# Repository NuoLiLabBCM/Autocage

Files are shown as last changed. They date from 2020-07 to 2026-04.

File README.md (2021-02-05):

# Autocage
A home-cage system for fully autonomous mouse behavioral and optogenetic experiments
## Features
- Automated home-cage training in challenging decision-making tasks with voluntary head-fixation
- Unsupervised optogenetic experiment to survey brain regions involved in behavior
- Running standalone, with GUI monitoring multiple parallel systems
- Protocols for automated training in voluntary head-fixation, delayed response task, and contingency reversals

## System Overview
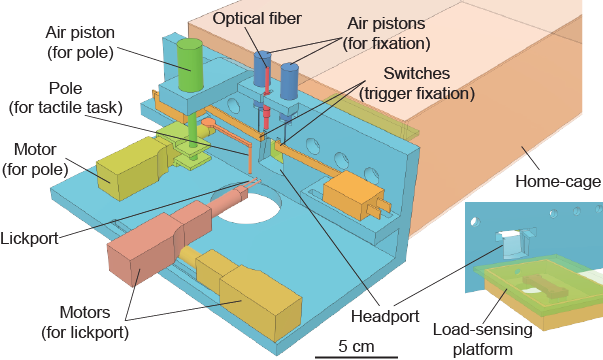
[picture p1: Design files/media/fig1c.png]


## Citation
Hao, Thomas, and Li. (2020) Fully autonomous mouse behavioral and optogenetic experiments in home-cage. https://doi.org/10.1101/2020.12.27.424480 

## Contact
Further information and requests should be directed to and will be fulfilled by the Lead Contact, Nuo Li (nuol@bcm.edu)

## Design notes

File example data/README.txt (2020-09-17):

/* There are six files in the folder for each mouse, They are:
 * PARAS.TXT:	parameters for task/trials
 * PARAF.TXT:	parameters for head-fixation
 * TRIALS.TXT:	data for each trial
 * EVENTS.TXT:	data for each event
 * EVENTST.TXT:	data for the detailed events for each trial
 * WEIGHT.TXT:	weight data read from scale (20 Hz sample rate, 
 * 				only record weights > 10 g); ONLY available in version 1.0
 */

/*************TRIALS.TXT*************
 * 
 * Each row is for one trial;
 * 
 * Column1: Unix time when the trial is finished;
 * Column2: trial number;
 * Column3: ProtocolType: 10-Fixation; 21-Sample; 22-Delay; 23-Optostim
 * Column4: subProtocol number: 0-fixation; 1~9-sample; 10~18-delay; 19-optostim
 *			0: from begining to head-fixation for 25 sec; Sample = 1.3 sec, random 
 *			   	delay (0.2~0.5 sec), no error trials
 *			1: autoLearn ON, random delay (0.3~0.6 sec), no error trials, 
 *				advance: reach 100 trials;
 *			3: autoLearn ON, random delay (0.3~0.6 sec), with error trials, advance: 
				reach 200 trials;
 *			4: autoLearn antiBias, random delay (0.3~0.6 sec), advance: performance > 75%
 *			13: antiBias, Delay = 0.3 sec, forced delay, advance: performance > 70%
 *			14: antiBias, Delay = 0.5 sec, forced delay, advance: performance > 70%
 *			15: antiBias, Delay = 0.8 sec, forced delay, advance: performance > 70%
 *			16: antiBias, Delay = 1.0 sec, forced delay, advance: performance > 70%
 *			17: antiBias, Delay = 1.3 sec, forced delay, advance: performance > 70%
 *			18: antiBias, Delay = 1.3 sec, forced delay, timeOut->4 sec, 
 *				advance: performance > 70%, fixation duration 30->60 sec
 *			19: antiBias, Delay = 1.3 sec, 15% trials with stimulation during sample/delay/response
 * Column5: Trial type: 0-right; 1-left; 2-either side
 * Column6: Trial outcome: 0-No Response; 1-Reward; 2-Time Out (error); 3-'Others'
 * Column7: Optostim flag: percentage of power (10, 30, 50, 70 100%) + stim epoch (1-stim during sample; 2-delay; 3-response)
 *			e.g., 11 means stim during sample with 10% power
 *			0 means no stimulation in this trial.
 * Column8: Forward/Backward motor position: 0-255
 * Column9: Left/Right motor position: 0-255 (70 is roughly the center)
 * Column10-end: States visited in this trial (see state machine coded in Arduino_Master.ino)
 * 
 **************TRIALS.TXT*************/

/*************EVENTS.TXT*************
 * 
 * Each row is one event recorded.
 * 
 * Column1: Time stamp for the event; if the event is 1, the time is Unix time; 
 * 			otherwise it is milisec after restart.
 * Column2: Event type: 1-Arduino restarted; 7-switchTriggered; 8-headfixation; 
 *			11-headfixation again immediately after release
			9-release1:timeup; 10-release2:escape; 12-release3:struggle
			20~22-user updating FB_motor_position, LR_motor_position and FB_final_position;
 * Column3: Event value: -1 means N/A, otherwise is value corresponding to the event.
 * 
 **************EVENTS.TXT*************/

/*************EVENTST.TXT*************
 * 
 * Each row is for one trial
 * 
 * Column1: Trial number;
 * Column2: Number of events in this trial;
 * Column3~end: pairs of event ID and timestamp
 * 				ID: 39-timeup (see state machine coded in Arduino_Master.ino for details); 
 *					0-left lickport in; 1-left lickport out; 
 *					2-right lickport in; 3-right lickport out;
 * 				timestamp: unit: 0.1 ms; 0 is start of a trial
 *
 **************EVENTST.TXT*************/

/*************WEIGHT.TXT*************
 *
 * Each row is a 2-sec data segment
 * 
 * Column1: Unix time when the data were sent;
 * Column2-41: weight data sampled at 20 Hz
 *
*************WEIGHT.TXT*************/

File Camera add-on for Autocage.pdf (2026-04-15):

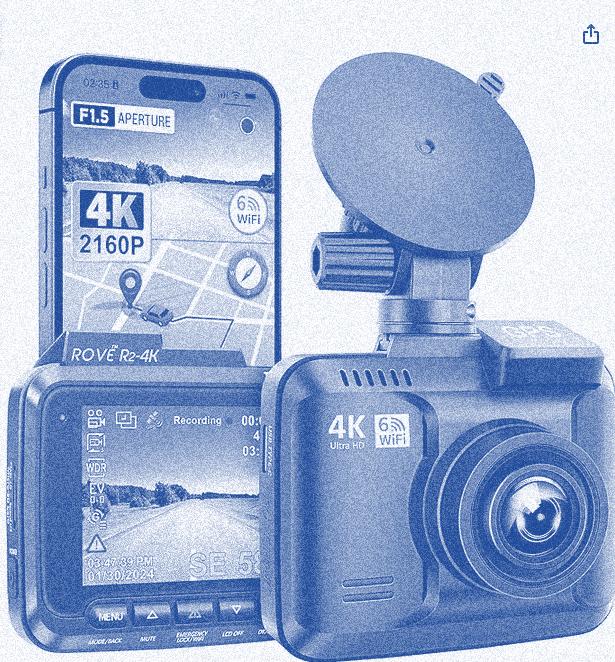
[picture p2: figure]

# add-on Camera to Autocage

# Part List:

Vender | Part # | Description | Unit Price
Amazon | R2-4K PRO | ROVE R2-4K PRO Dash Cam, Supports 512GB Max | $129.99
Amazon | MB-MD512SA/AM | SAMSUNG PRO Plus microSD Memory Card + Adapter, 512GB | $49.99
Amazon | UTC1211USP-WH | Amazon Basics 12W One Port USB-A Wall Charger (2.4A) Pack of 2 | $5.1
ThorLabs | FGB25 | Ø25 mm BG3 Colored Glass Bandpass Filter, 315 - 445 nm and 715 - 1095 nm | $40.70
ThorLabs | LA1134 | N-BK7 Plano-Convex Lens, Ø1", f = 60 mm, Uncoated | $24.43
ThorLabs | SM1L03 | SM1 Lens Tube, 0.30" Thread Depth, One Retaining Ring Included | $13.15
DigiKey | 365-1056-ND | EMITTER IR 890NM 150MA T 1 3/4 | $1.13
DigiKey | CF14JT39R0CT-ND | RES 39 OHM 5% 1/4W AXIAL | $0.04
| | Total | $264.93

# Hardware Setup

### - Camera Setup:

- Get a ROVE R2-4K PRO dash cam.
- Mount a lens (f=60mm) with a filter to the camera. The filter is for filtering out the masking LED light (RED).
- Insert a SAMSUNG 512G microSD memory card.
- Power on the dash cam.
- Follow the user manual to setup the camera settings via Setting Menu. You can do the settings either on the camera screen directly, or on your smartphone by connecting to the dash cam Wi-Fi and using ROVE APP.
- Key settings:
- Video Resolution: 1080P 1920x1080 @30FPS. (with 512G SD Card, you can get about 5 days’ data).
- Loop Recording: 1-Min,3-Min, 5Min or 10 Min.

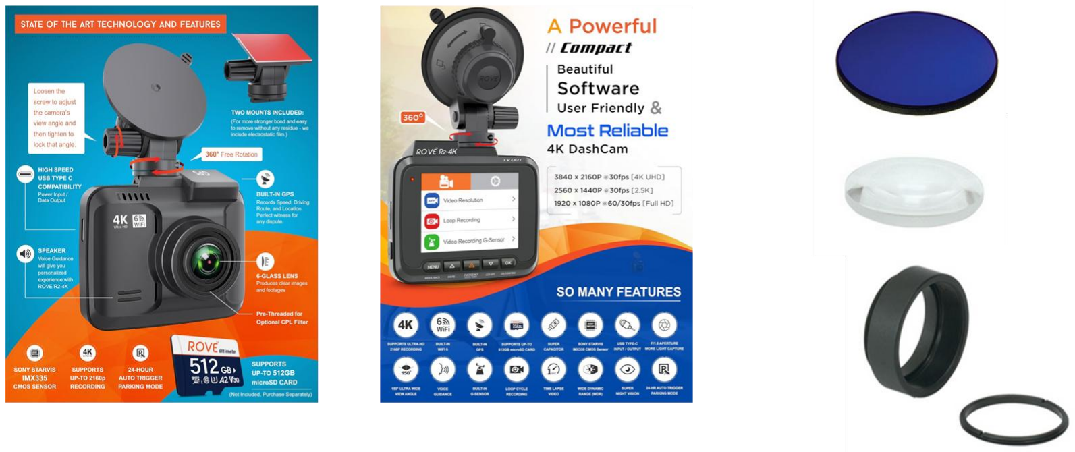
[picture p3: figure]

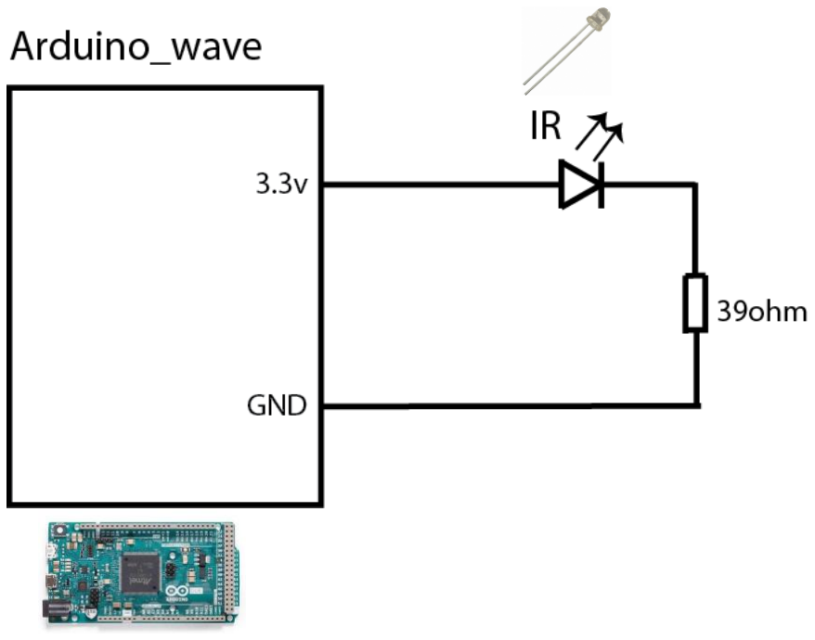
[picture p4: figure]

- IR Illuminator
- Get an Infrared Emitter and a 39 Ohm resistor.
- Assemble and connect the IR Illuminator to the existing Arduino DUE board (wave) as shown in the diagram.

# Add-on Camera layout inside Autocage

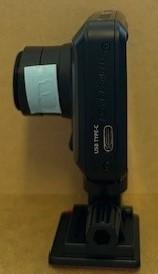
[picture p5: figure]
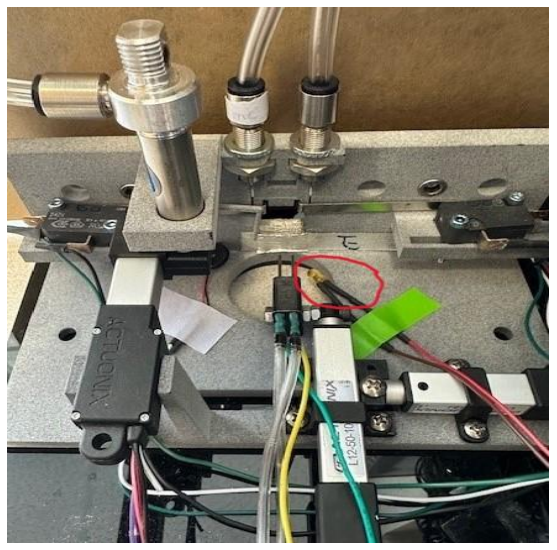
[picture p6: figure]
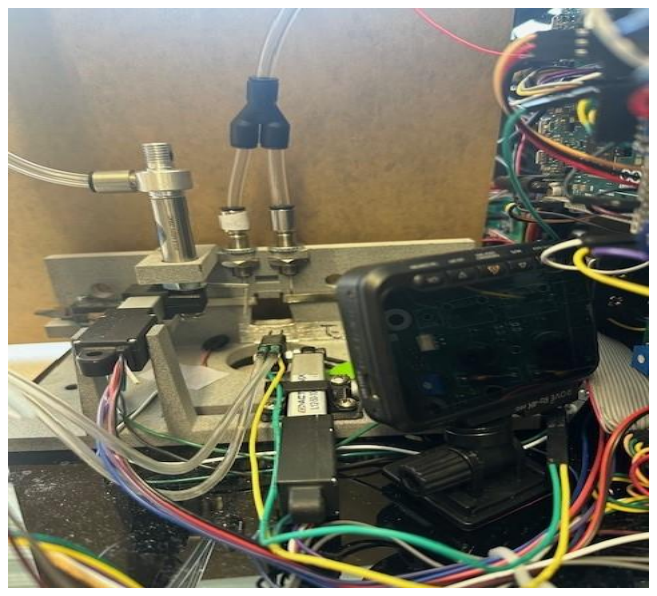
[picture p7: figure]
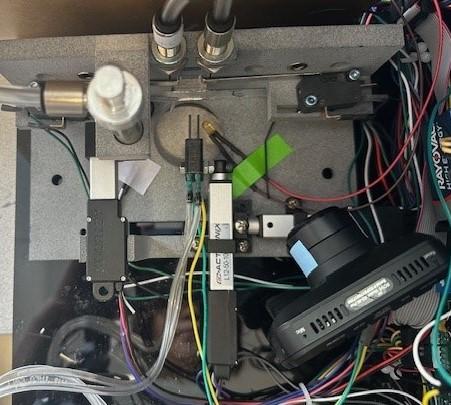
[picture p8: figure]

IR Illuminator | Front view | Top view | Side view

# Video Example

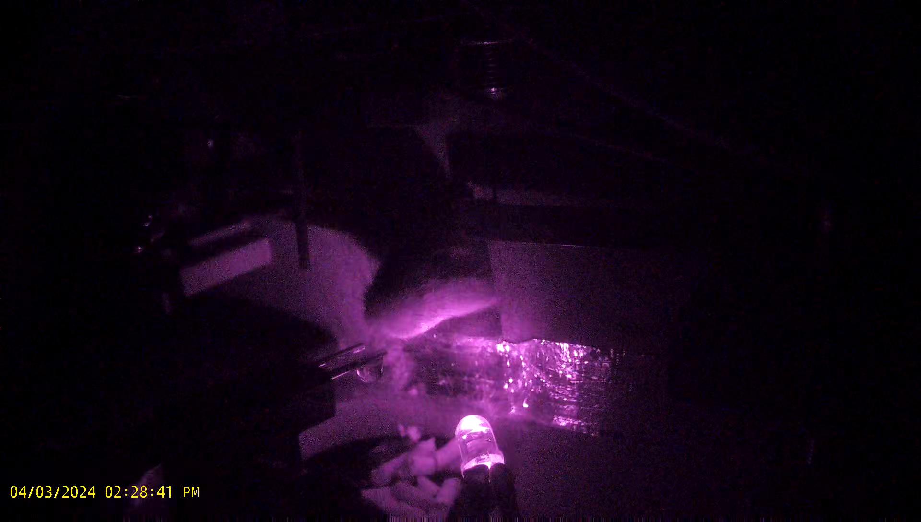
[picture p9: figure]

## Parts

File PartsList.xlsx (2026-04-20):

Part | Vendor | Item no. | Item description | Qty per Cage | Unit Price | Each Cage | Note
Enclosure | McMaster-carr | 8505K745 | Scratch-Resistant Acrylic BLACK 1/8 | 1.167 | $45.58 | $53.18
 | McMaster-carr | 8505K758 | Scratch-Resistant Acrylic BLACK 1/4 | 0.250 | $83.02 | $20.75
 | HARTFIEL AUTOMATION INC | 25-2525-BLACK | 20" LONG 25mm Construction Rail with 1/4-20 Tap (25-7061 Left) and Cut to Length(25-7005) | 2.000 | $12.70 | $25.40
 | HARTFIEL AUTOMATION INC | 25-2525-BLACK | 9" LONG 25mm Construction Rail with 1/4-20 Tap (25-7061 Left)+ Cut to Length(25-7005) | 6.000 | $8.43 | $50.58 | 8020 parts
 | HARTFIEL AUTOMATION INC | 25-3382 | 25 S 1/4-20 ECONOMY T-NUT [BLACK] | 16.000 | $0.37 | $5.92
 | McMaster-carr | 92311A540 | 18-8 Stainless Steel Cup-Point Set Screw,1/4"-20 Thread, 3/4" Long | 0.120 | $10.77 | $1.29
 | McMaster-carr | 47065T239 | Silver Corner Bracket, 2" Long for 1" High Rail T-Slotted Framing | 2.000 | $8.54 | $17.08
Pneumatic Actuator for Headfixation | McMaster-carr | 6604K11 | Miniature Threaded-Body Air Cylinder Single Acting, 1/4" Bore, 3/8" OD, 1/4" Stroke Length | 2.000 | $85.48 | $170.96 | Piston for head-fixation
 | McMaster-carr | 91843A109 | Knurled Panel Nut 3/8"-32 Thread Size | 2.000 | $3.55 | $7.10
 | McMaster-carr | 5779K246 | Push-to-Connect Tube Fitting for Air Straight Adapter, for 1/4" Tube OD x 10-32 Thread Male | 3.000 | $5.77 | $17.31
 | McMaster-carr | 5779K44 | Push-to-Connect Tube Fitting for Air Wye Connector, for 1/4" Tube OD | 1.000 | $6.70 | $6.70
 | FESTO | 557773 | Prop-press reg VPPE-3-1-1/8-10-010-E1 | 1.000 | $725.11 | $725.11 | Analog pressure regulator
 | FESTO | 8078242 | NEBA-M12G5-U-2.5-N-LE5 | 1.000 | $20.22 | $20.22
 | McMaster-carr | 5225K564 | 90 Degree Swivel Elbow, for 6 mm Tube OD x 1/8 BSPP Male | 1.000 | $6.77 | $6.77
 | McMaster-carr | 5779K425 | 90 Degree Swivel Elbow, for 1/4" Tube OD x 1/8 BSPT Male | 1.000 | $7.95 | $7.95
 | McMaster-carr | 9836K21 | Muffler with 1/8 BSPT Male Steel Fitting | 1.000 | $2.63 | $2.63
 | McMaster-carr | 90272A357 | Zinc-Plated Steel Pan Head Phillips Screw, 8-32 Thread, 2-1/4" Long | 0.080 | $8.60 | $0.69
 | FESTO | 196847 | Solenoid valve CPE10-M1BH-3GL-QS-6 | 1.000 | $196.00 | $196.00 | 3/2-way solenoid valve
 | BIBMA | 010.5-NRP | Single-acting pivot (spring-return) non-rotating hexagon rod pneumatic air cylinder - Bimba (Original line air cylinder series) - 7/16" bore (B7/16") - 1/2" stroke (S1/2") - Rear pivot mounting - #10-32 UNF-2A (male) threaded rod + 3/8-24 UNF-2A threaded + 7/16-20 UNF-2 threaded - #10-32 threaded pneumatic port - Stainless steel rod | 1.000 | $34.97 | $34.97 | https://shop.ifp1.com/products/010.5-NRP
 | McMaster-carr | 93181A411 | Aluminum Hex Nut, 10-32 Thread Size | 0.020 | $8.52 | $0.17
 | McMaster-carr | 62005K124 | 1-way FLOW control VALVE | 2.000 | $15.10 | $30.20
Pole Machenism | FESTO | 153023 | push-in fitting 1/8 | 0.100 | $38.80 | $3.88
 | FESTO | 153321 | push-in fitting M7 male | 0.100 | $24.60 | $2.46
 | McMaster-carr | 5225K87 | Push-to-Connect Tube Fitting for Air, Wye Connector, for 6 mm Tube OD | 1.000 | $7.28 | $7.28
 | FESTO | 8086628 | MS2-LR-M5-D6-AR-BAR-B | 1.000 | $36.26 | $36.26
 | McMaster-carr | 7880T392 | Push-to-Connect Tube Fitting 6mm Tube OD, M5 Pipe | 2.000 | $2.29 | $4.58
Switch | McMaster-carr | 91292A020 | 18-8 Stainless Steel Socket Head Screw, M3 x 0.5 mm Thread, 25 mm Long | 0.040 | $9.51 | $0.38
 | McMaster-carr | 90592A085 | Steel Hex NutMedium-Strength, Class 8, M3 x 0.5 mm Thread | 0.040 | $1.43 | $0.06
 | Mouser | 540-D439-V1ML-G2 | Basic / Snap Action Switches SPDT QC Straight Lever 5A 125-250V | 2.000 | $5.74 | $11.48 | Switches (left and right)
weighting Stage | Phidgets | 3139_0 | Single Point Load Cell- 100g | 1.000 | $7.00 | $7.00 | Load cell
 | Mouser | 474-SEN-13879 | SparkFun Load Cell Amplifier - HX711 | 1.000 | $10.65 | $10.65 | Amplifier
 | McMaster-carr | 89015K111 | Multipurpose 6061 Aluminum Sheet, 0.016" Thick, 2" x 24" | 0.111 | $4.51 | $0.50
 | McMaster-carr | 95836A259 | 18-8 Stainless Steel Pan Head Phillips Screws, M2.5 x 0.45 mm Thread, 12mm Long | 0.080 | $10.03 | $0.80
Motors | Actuonix | L12-50-100-12-I | L12 12V 50mm 100:1 Analog Miniature Linear Actuator | 1.000 | $90.00 | $90.00 | for lickport (forward-backward)
 | Actuonix | L12-30-50-12-I | L12 12V 30mm 50:1 Analog Miniature Linear Actuator | 2.000 | $90.00 | $180.00 | for lickport (left-right) and pole
 | McMaster-carr | 91772A144 | 18-8 Stainless Steel Pan Head Phillips Screw, 6-32 Thread, 1/4" Long | 0.040 | $6.55 | $0.26
 | McMaster-carr | 91772A194 | 18-8 Stainless Steel Pan Head Phillips Screw, 8-32 Thread, 1/2" Long | 0.010 | $10.86 | $0.11
 | McMaster-carr | 91290A176 | Alloy Steel Socket Head Screw, M4 x 0.7 mm Thread, 25 mm Long | 0.020 | $10.41 | $0.21
 | McMaster-carr | 90593A003 | Black-Oxide Steel Hex Nut, Medium-Strength, Class 8, M4 x 0.7 mm Thread | 0.030 | $13.54 | $0.41
 | McMaster-carr | 91772a146 | 18-8 Stainless Steel Pan Head Phillips Screw, 6-32 Thread, 3/8" Long | 0.020 | $6.46 | $0.13
 | McMaster-carr | 92150A106 | Washer Nylon Plastic, Number 6 Screw Size, NAS1515-H06L | 0.040 | $9.20 | $0.37
Buzzer | Mouser | 490-CPE-163 | Piezo Buzzers & Audio Indicators buzzer | 1.000 | $1.12 | $1.12
SD Card | Mouser | 485-1141 | Adafruit Assembled Data Logging shield for Arduino | 1.000 | $13.95 | $13.95 | Data logging shield
 | Mouser | 485-85 | Shield stacking headers for Arduino (R3 Compatible) | 1.000 | $1.95 | $1.95
 | Mouser | 485-1294 | SD/MicroSD Memory Card (8 GB SDHC) | 1.000 | $9.95 | $9.95
 | Mouser | 485-380 | CR1220 12mm Diameter - 3V Lithium Coin Cell Battery - CR1220 | 1.000 | $0.95 | $0.95
Arduino | Mouser | 545-U050-006 | USB 2.0 to micro B Cable,6ft | 1.000 | $6.37 | $6.37
 | Mouser | 612-RA1H1C112R | Rocker Switches 16A 125VAC Horiz PCB Off-On | 1.000 | $1.02 | $1.02
 | Mouser | 490-SWI25-12-N-P5 | Wall Mount AC Adapters 25.2W 12V 2.1A | 1.000 | $21.10 | $21.10
 | Mouser | 490-SWI25-24-N-P5 | Wall Mount AC Adapters 25.2W 24V 1.05A | 1.000 | $29.34 | $29.34
 | Mouser | 485-1352 | 4-Way 2.1mm DC Barrel Jack Splitter | 1.000 | $4.95 | $4.95 | for version 1 cage
 | Mouser | 485-1351 | 2-Way 2.1mm DC Barrel Jack Splitter | 1.000 | $2.95 | $2.95 | for version 2 cage
 | Mouser | A000062 | Arduino Due 32bit ARM Microcontroller | 3.000 | $46.77 | $140.31 | only need one for version 2 cage
 | Mouser | 558-DMO063 | Solid State Relay | 3.000 | $33.82 | $101.46 | 2 for reward valves; 1 for 3/2 solenoid
Reward | Lee Co. | LHDA1233215H | solenoid valve for reward | 2.000 | $74.08 | $148.16
 | Amazon | B07QGDLJ15 | Miniature Toggle Switch ON/ON 5A 120V 2A 250V | 0.250 | $7.66 | $1.92
Optogenetics & Masking LED | Mouser | 485-935 | MCP4725 Breakout Board - 12-Bit DAC w/I2C | 1.000 | $4.95 | $4.95 | DAC for Laser
 | Mouser | COM-13716 | FemtoBuck LED Driver | 1.000 | $8.95 | $8.95 | Masking flash LED and driver
 | LexonStar | SP-01-R5 | Red (627nm) Rebel LED on a SinkPAD-II 20mm Star Base - 53 lm @ 350mA | 1.000 | $7.59 | $7.59
Lickport Detector | Screaming Circuts |  | Lickport Detector | 1.000 | $90.00 | $90.00 | Custom-made
 | Mouser | 81-RDEC71E474K0P1H3B | 0.47uf Multilayer Ceramic Capacitors | 2.000 | $0.61 | $1.22
 | Amazon | B0CBMMTKVM | 9V Battery Boxes | 0.500 | $7.99 | $4.00
 | Amazon | B0B72DBKVF | 9v Battery | 0.167 | $25.37 | $4.23
Custom breakout PCB board | Sunstone Circuit | BCM-NL-HCT001 |  | 1.000 | $15.00 | $15.00 | Custom breakout PCB board
 | Digikey | 732-5394-ND | CONN HEADER VERT 6POS 2.54MM | 1.000 | $0.47 | $0.47
 | Digikey | 732-2099-ND | Connector Header Through Hole, Right Angle 16 position 0.100" (2.54mm) | 1.000 | $0.71 | $0.71
 | Digikey | 1N4004DICT-ND | DIODE GEN PURP 400V 1A DO41 | 3.000 | $0.08 | $0.23
 | Mouser | 485-373 | Adafruit Accessories 2.1mm DC Barrel Jack | 2.000 | $0.95 | $1.90
 | Mouser | 565-4969 | Test Leads 20 AWG LEADS | 1.000 | $11.89 | $11.89 | for version 1 cage
 | Mouser | 523-31-10-RFX | RF Connectors / Coaxial Connectors | 1.000 | $4.02 | $4.02 | for version 2 cage
 | Amazon | B07PKKY8BX | MCIGICM 10pcs Male Header Pin, 40 Pin Header Strip (2.54 mm) | 0.200 | $4.99 | $1.00
3D print parts | 3D hubs | Headport.stl | Headport | 1.000 | $116.90 | $116.90
 | 3D hubs | Lickport Holder.stl | Lickport Holder | 1.000 | $1.00 | $1.00
 | 3D hubs | mechanical_pole.stl | Pole | 1.000 | $1.00 | $1.00
 | 3D hubs | motor_fix_lickport.stl | Lickport Motor holder | 1.000 | $1.00 | $1.00
 | 3D hubs | motor_fix_piston.stl | Pole motor holder | 1.000 | $1.00 | $1.00
 | 3D hubs | Switch_holder.stl | Switch Holder | 1.000 | $1.00 | $1.00
 | 3D hubs | Weighting_Stage_Bottom.stl | WeightingStageTop | 1.000 | $2.74 | $2.74
 | 3D hubs | Weighting_Stage_Top.stl | WeightingStageBottom | 1.000 | $3.10 | $3.10
 | Cole-Parmer | EW-07944-24 | SYRINGE 30ML LUER-LOK 25/PK | 0.080 | $40.00 | $3.20
water Reservoir | Cole-Parmer | EW-50109-75 | F LUERXBARB 1/16 PP 10/PK | 0.200 | $7.60 | $1.52
 | McMaster-carr | 47065T821 | Single 4-Slot Rail, Silver, 1" High x 1" Wide, Solid, 4" Long | 1.000 | $5.53 | $5.53
 | McMaster-carr | 3035T67 | Plate for 1/4"-20 Thread Size 1-1/8" ID Aluminum U-Bolt | 1.000 | $2.99 | $2.99
home cage | Ancare Corp | N10HT | Hi-Temp Polycarbonate Cage Bottom, Mouse, 11.5" x 7.5" x 5"H | 0.050 | $329.00 | $16.45
 | Ancare Corp | N10MBTRH | Hi-Temp Polycarbonate Micro-Filter Top with Perforated Retainer, Mouse, REDUCED HEIGHT | 0.050 | $439.00 | $21.95
 | McMaster-carr | 5233K51 | Clear Masterkleer Soft PVC Plastic Tubing, 1/16" ID, 1/8" OD | 5.000 | $0.29 | $1.45
 | McMaster-carr | 8987K47 | 304 Stainless Steel Tubing, 0.05" OD, 0.006" Wall Thickness | 0.111 | $19.71 | $2.19
 | McMaster-carr | 50315K24 | Firm Polyurethane Rubber Tubing, 4 mm ID, 6 mm OD, Opaque | 3.000 | $0.51 | $1.53
 | McMaster-carr | 5233K52 | Clear Masterkleer Soft PVC Plastic Tubing, 1/8" ID, 1/4" OD | 1.500 | $0.24 | $0.36
 | McMaster-carr | 5648K25 | Firm Polyurethane Tubing for Air and Water 5/32" ID, 1/4" OD, Opaque Green | 2.500 | $0.68 | $1.70
 | McMaster-carr | 47065T905 | T-Slotted Framing End-Feed Nut for 1" and 25 mm High Rail, 1/4"-20 Thread | 0.240 | $7.83 | $1.88
 | Pololu | 4576 | Ribbon Cable with Pre-Crimped Terminals 10-Color M-F 6" | 1.000 | $1.29 | $1.29
 | Pololu | 4577 | Ribbon Cable with Pre-Crimped Terminals 10-Color M-M 6" | 1.000 | $1.29 | $1.29
 | Pololu | 4578 | Ribbon Cable with Pre-Crimped Terminals 10-Color F-F 12" | 1.000 | $2.39 | $2.39
 | Pololu | 4579 | Ribbon Cable with Pre-Crimped Terminals 10-Color M-F 12" | 1.000 | $2.39 | $2.39
 | Pololu | 4580 | Ribbon Cable with Pre-Crimped Terminals 10-Color M-M 12" | 1.000 | $2.39 | $2.39
 | Pololu | 4581 | Ribbon Cable with Pre-Crimped Terminals 10-Color F-F 24" | 1.000 | $4.25 | $4.25
 | Pololu | 4582 | Ribbon Cable with Pre-Crimped Terminals 10-Color M-F 24" | 1.000 | $4.25 | $4.25
Miscellaneous | Pololu | 1900 | 0.1" (2.54mm) Crimp Connector Housing:1x1-Pin 25-Pack | 1.000 | $1.29 | $1.29
 | Pololu | 1901 | 0.1" (2.54mm) Crimp Connector Housing: 1x2-Pin 25-Pack | 1.000 | $1.49 | $1.49
 | Pololu | 1902 | 0.1" (2.54mm) Crimp Connector Housing: 1x3-Pin 25-Pack | 0.200 | $1.69 | $0.34
 | Pololu | 1903 | 0.1" (2.54mm) Crimp Connector Housing: 1x4-Pin 10-Pack | 0.500 | $1.29 | $0.65
 | Pololu | 1904 | 0.1" (2.54mm) Crimp Connector Housing: 1x5-Pin 10-Pack | 0.100 | $1.49 | $0.15
 | Pololu | 1905 | 0.1" (2.54mm) Crimp Connector Housing: 1x6-Pin 10-Pack | 0.100 | $1.69 | $0.17
 | Digikey | A364B-4-ND | HEATSHRINK 3/64 IN X 4FT BLACK | 0.500 | $1.57 | $0.79
 | Digikey | A116B-4-ND | HEATSHRINK 1/16 IN X 4FT BLACK | 0.500 | $1.60 | $0.80
 | Digikey | A316B-4-ND | HEATSHRINK 3/16 IN X 4FT BLACK | 0.250 | $2.16 | $0.54
 | Amazon | B0146DJR9Q | Gikfun 100 Pairs Suitable for 22AWG Cable Male and Female Pins Connector | 0.200 | $7.88 | $1.58
 | Amazon | B07BDLZSWR | 5pcs 40cm F/F IDC 2x3 6Pin 2.54mm Cable | 0.100 | $9.05 | $0.91
 | Amazon | B07BHFQT41 | 2-Pack 16" 40cm F/F IDC 2x8 16P 2.54mm cable | 0.250 | $7.95 | $1.99
 | Amazon | B07MMBRF48 | 6-Pack Black 1m 3.3ft BNC Male to BNC Male Jumper Cable with Black Connector | 0.167 | $14.98 | $2.50 | for version 1 cage
 | McMaster-carr | 76925A5 | Conductive Aluminum Foil Electrical Tape 2" Wide, 15 Feet Long | 0.022 | $22.94 | $0.51
 | McMaster-carr | 5759K36 | Flexible Magnet with Holding Power on One Face, Rubber Adhesive Back, 1/32" Thick, 3/4" Wide | 12.000 | $0.60 | $7.20
 | McMaster-carr | 74765A35 | Instant-Bond Adhesive, Gel, Loctite454, 0.7 FL. oz. Tube | 0.050 | $33.67 | $1.68
 | McMaster-carr | 92745A321 | Male-Female Threaded Hex Standoff, 1/4" Hex Size, 3/8" Long, 4-40 to 4-40 Size Thread | 8.000 | $0.47 | $3.76 | need only 4 for version 2 cage
 | McMaster-carr | 92745A320 | Male-Female Threaded Hex Standoff, 1/4" Hex Size, 1/4" Long, 4-40 to 4-40 Size Thread | 4.000 | $0.47 | $1.88 | for version 1 cage
 | McMaster-carr | 92745A324 | Male-Female Threaded Hex Standoff, 1/4" Hex Size, 3/4" Long, 4-40 to 4-40 Size Thread | 4.000 | $0.46 | $1.84
 | McMaster-carr | 90176A155 | Nylon Unthreaded Spacers 1/2" OD, 1/4" Long, Black | 0.080 | $4.26 | $0.34
 | McMaster-carr | 94735A763 | Nylon Pan Head Screws Phillips, 1/4"-20 Thread, 1/2" Long | 0.020 | $14.27 | $0.29
 | McMaster-carr | 94735A717 | Nylon Pan Head Screws Phillips, 4-40 Thread, 1/4" Long | 0.270 | $8.56 | $2.31
 | McMaster-carr | 94735A727 | Nylon Pan Head Screws Phillips, 6-32 Thread, 1/4" Long | 0.070 | $8.72 | $0.61
 | McMaster-carr | 91772A537 | 18-8 Stainless Steel Pan Head Phillips Screw, 1/4"-20 Thread, 1/2" Long | 0.120 | $14.80 | $1.78 | for frame
 | McMaster-carr | 91772A535 | 18-8 Stainless Steel Pan Head Phillips Screw, 1/4"-20 Thread, 3/8" Long | 0.140 | $9.24 | $1.29 | for frame
 | McMaster-carr | 92196A537 | 18-8 Stainless Steel Socket Head Screw1/4"-20 Thread Size, 1/2" Long | 0.040 | $20.71 | $0.83 | for home cage
 | McMaster-carr | 91845A029 | 18-8 Stainless Steel Hex Nut, 1/4"-20 Thread Size | 0.020 | $5.34 | $0.11 | for home cage
 | McMaster-carr | 94323A840 | Nylon Raised-Head Thumb Screws, 1/4"-20 Thread Size, 3/4"Long | 0.040 | $18.19 | $0.73 | for headport

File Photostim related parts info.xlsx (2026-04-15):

Maker | Laser/LED Model | Driver model | Color | Wavelength | LaserOff voltage (V) | LaserMax voltage (V) | Stock(set)
Ultralasers | MRL-III-633L-50mW, BJ00699 | PSU-III-FDA | Red | 633 | 0.8 | 4.5 | 10
 | MRL-III-635L-200mW, CF61470 | PSU-III-FDA | Red | 638 | 0.8 | 4.5 | 7
ThorLabs | M625F2 | LEDD1B | Red | 625 | 0 | 5 | 3
 | M595F2 | LEDD1B | PC Amber | 595 | 0 | 5 | 1
Item | Description | Stock | Note
Fiber Coupler | FC/PC 635nm | 6 | for MRL-III-635L-200mW
Fiber | M82L005 | 10 | for MRL-III-635L-200mW
 | M79L005 | 12 | for MRL-III-633L-50mW
 | M98L01 | 4 | for MRL-III-633L-50mW

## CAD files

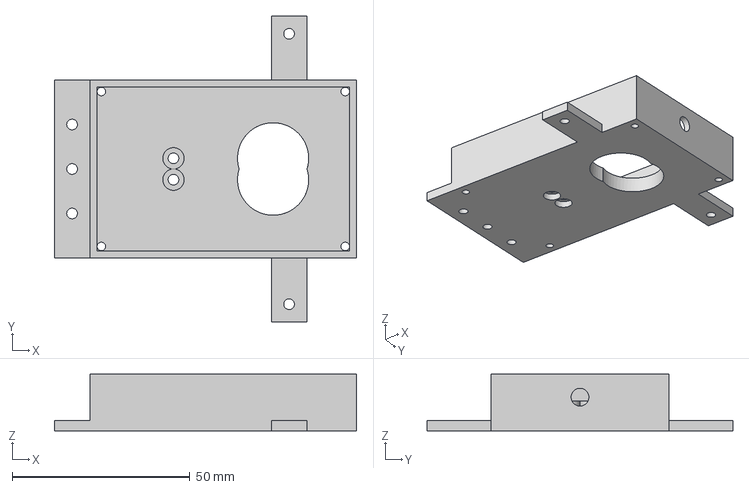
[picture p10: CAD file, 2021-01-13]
Design files/Weighting_Stage_Bottom.iges
85.0 x 86.0 x 16.0 mm

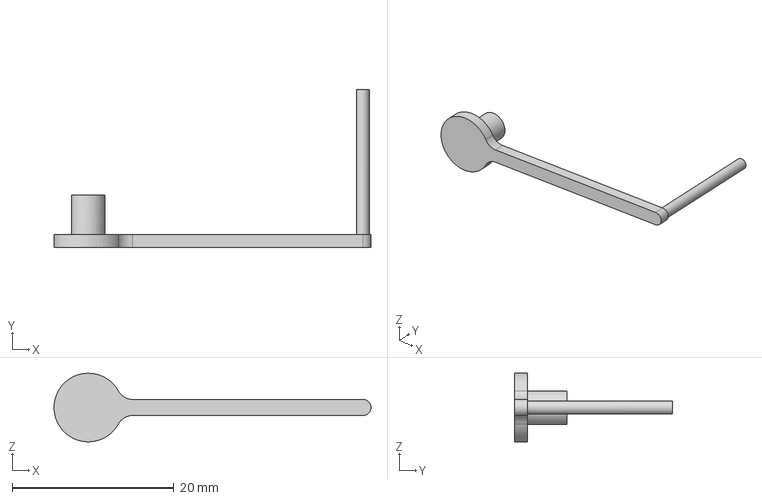
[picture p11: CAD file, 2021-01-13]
Design files/mechanical_pole.iges
39.2 x 19.6 x 8.50 mm

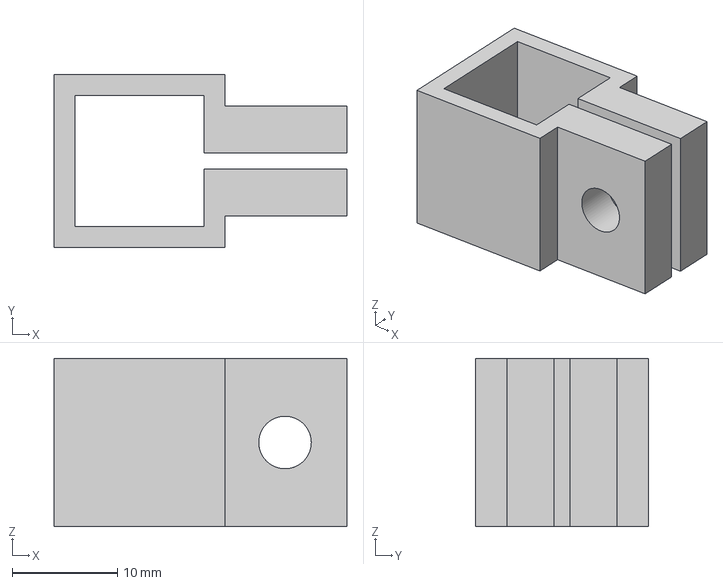
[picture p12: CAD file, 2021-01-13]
Design files/motor_fix_piston.iges
27.9 x 16.5 x 16.0 mm

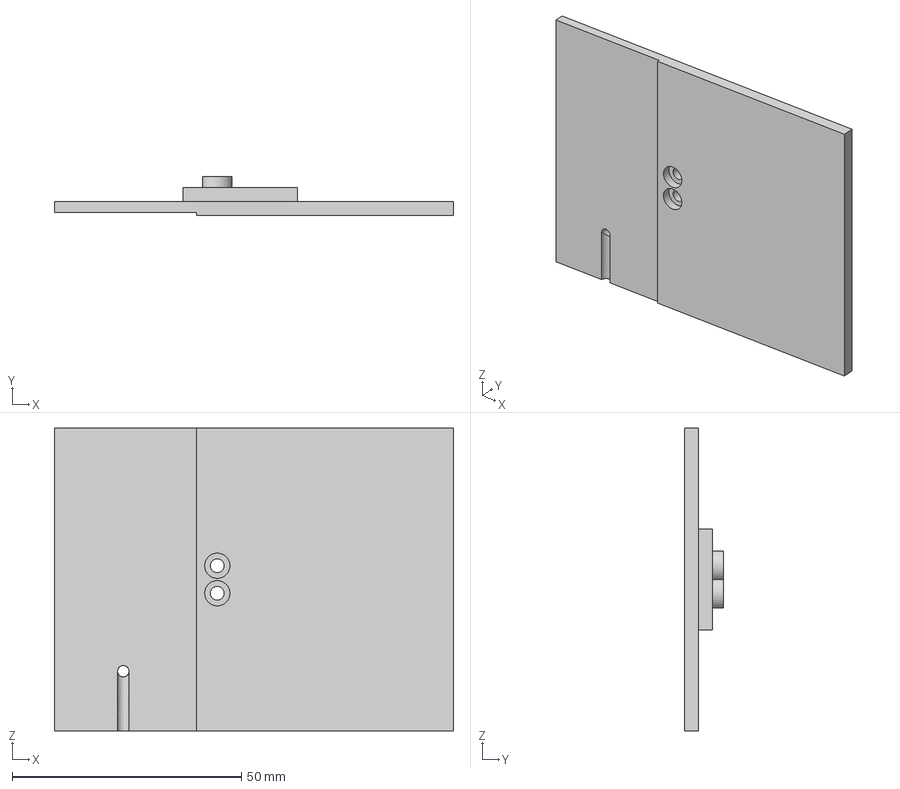
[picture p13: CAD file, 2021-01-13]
Design files/Weighting_Stage_Top.iges
87.0 x 8.40 x 66.0 mm

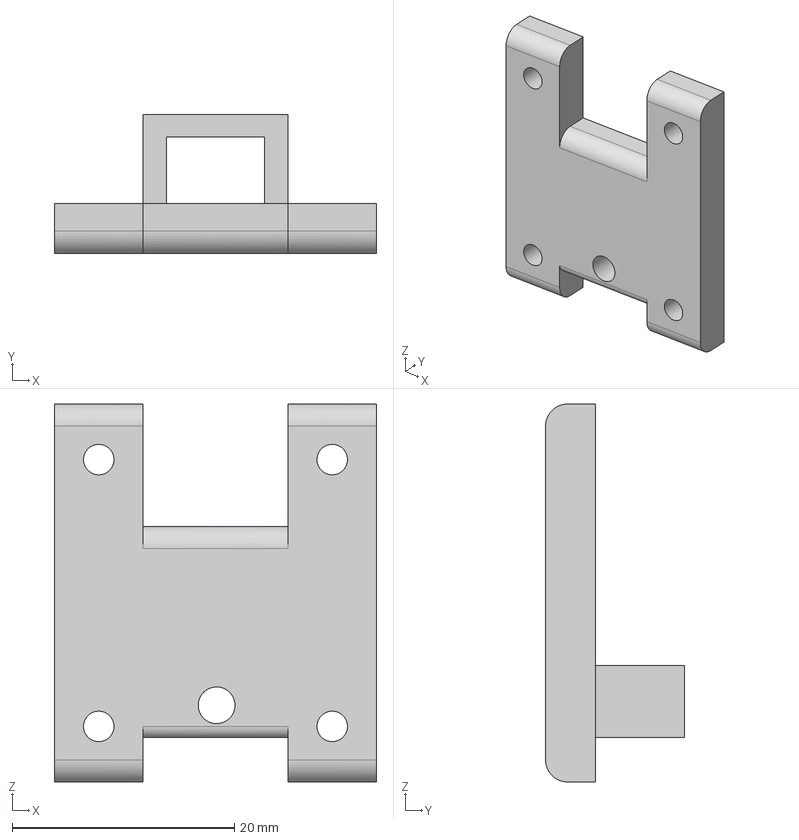
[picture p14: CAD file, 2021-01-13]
Design files/motor_fix_lickport.iges
29.0 x 12.5 x 34.0 mm

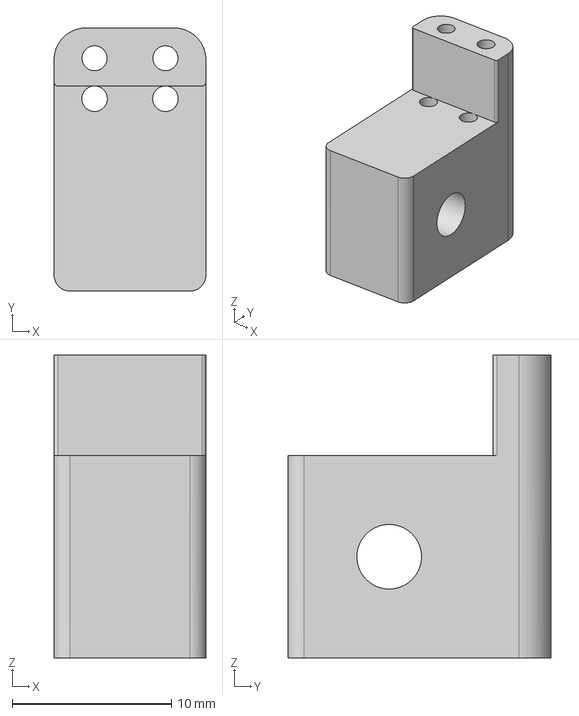
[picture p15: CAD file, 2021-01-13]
Design files/Lickport Holder.iges
9.53 x 16.5 x 19.0 mm

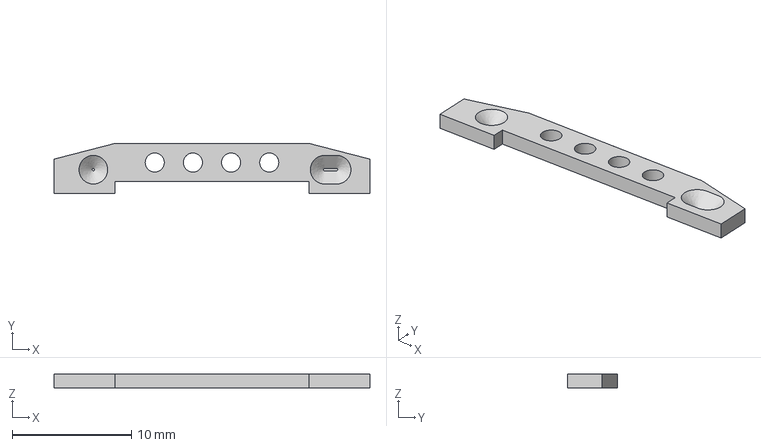
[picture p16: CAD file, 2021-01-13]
Design files/Headbar.iges
26.5 x 4.20 x 1.20 mm

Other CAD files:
Design files/Switch_holder.iges
Design files/Headport.iges
Design files/Headbar.stl
Design files/Headport.stl
Design files/Lickport Holder.stl
Design files/Switch_holder.stl
Design files/Weighting_Stage_Bottom.stl
Design files/Weighting_Stage_Top.stl
Design files/mechanical_pole.stl
Design files/motor_fix_lickport.stl
Design files/motor_fix_piston.stl

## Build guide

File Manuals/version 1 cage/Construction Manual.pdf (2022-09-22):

### Automated Home-cage System Construction Manual

## Contents

### 1. Build an Enclosure

- Get six 9"construction rails (XE25L09) and two 20" rails (XE25L20). Lay out three of the 9” rails in a "U" shape, with the two side rails laying on top of the bottom rail (Fig1.1). Join the rails using two setscrews (SS25S075) and drop-in T-nuts (XE25T1). Repeat above steps to make another "U" shape.
- Connect two ‘U’ shape together with 20" construction rails at top corners. Join the rails with two setscrews and drop-in T-nuts in one side and fasten with two right angle brackets (AB90H), drop-in T nuts, and 1/4-20 screws in the other side (Fig.1.2).
- Cut one 9"x22" thick acrylic board (8505K758) and fix it at the bottom of the enclosure using ¼-20 screws and drop-in T-nuts. Cut two 9"x10", two 10”x22" and one 9"x22" thin acrylic boards (8505K745). Attach one 9"x10" and one 10"x22" board on the back and right side of the enclosure, respectively, with ¼-20 screws and drop-in T-nuts (Fig1.3).
- Cut ten 9" and four 22" strips of magnetic tape. Pair together and place adhesive of one of the two paired strips on left side and front rails. Remove adhesive on other strip of magnetic tape pairs. Carefully align 9"x10" and 10"x22" acrylic sheets with their respective sides. Press firmly to secure adhesive to edges of acrylic sheet.
- Cut a rectangular hole (7"x7") on the 9"x22" board and cover it with metal mesh. Place the board on the top to cover the enclosure (Fig1.4).
Fig. 1.1 | Fig.1.2 | Fig.1.3 | Fig.1.4

### 2. Components on the Enclosure Side Boards

- Get an analog pressure regulator (FESTO, 557773). Screw one L-shape push-in-fit (5225K564) in the inlet hole, and another L-shape push-in-fit (5779K425) in the outlet hole. Screw a silencer (9836K21) at the exhaust hole (hole no. 3).
- Get a manual pressure regulator (LR-M5-D-7-MICRO) and fit with two push-in fitting (QSM-M5-6).
- Fix the above two regulators on the back board of the enclosure. (Fig.2.1).
- Get a custom breakout PCB board (BCM-NL-HCT001). Solder three solid state relays (CC1139-ND), one HX711 amplifier (SparkFun, SEN-13879), one MCP4725 DAC (Adafruit, 935), one LED driver (SparkFun, SS25S075), one 6-pin 2x3 box header connector (JP1), one 16-pin 2x8 box header connector (JP2), one 9-pin (JP4), one 6-pin (JP6) and one 16-pin 2x8 straight header connectors (JP5), on the PCB board (Fig.2.2).

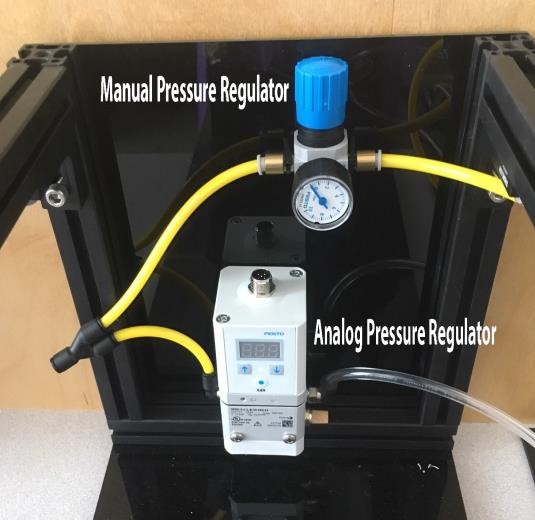
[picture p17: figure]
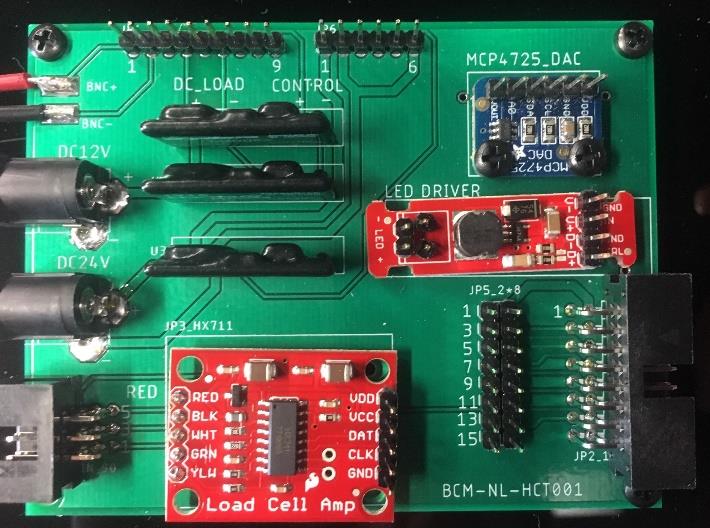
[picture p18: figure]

Fig.2.1 | Fig. 2.2
- Fix three Arduino boards (Mouse, A000062), one custom lickometer PCB, one 9V battery case, one 3/2-way solenoid valve (FESTO, 196847) and custom breakout PCB on the enclosure right board (Fig.2.3). Assemble a SD card shield (https://www.adafruit.com/product/1141), connect DIO5 to CD via a jump wire, and insert the SD card shield into Arduino_Master board.

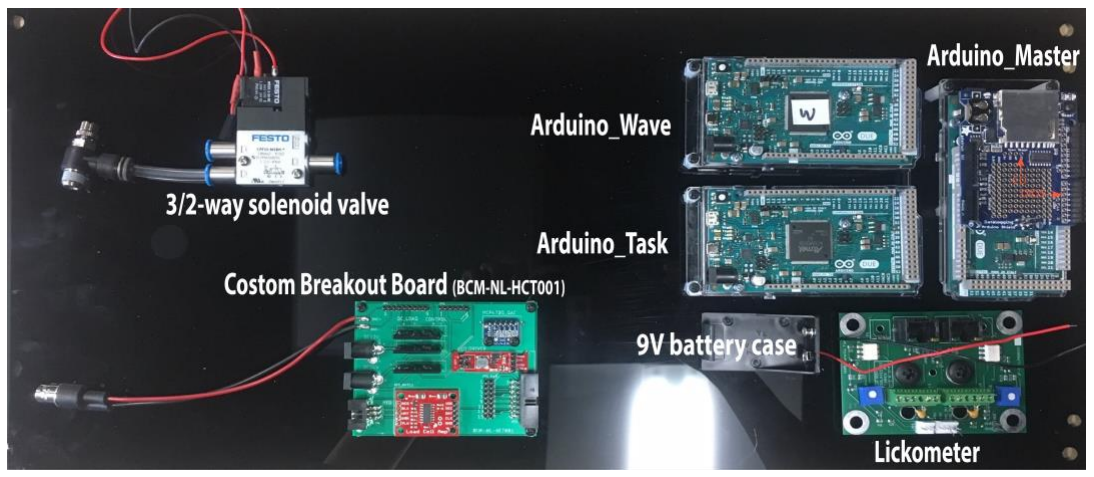
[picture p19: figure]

Fig. 2.3

### 3. Lickport Station

- Cut two 18”, two 9”, and two 2” pieces of 1/32” plastic tubing (Tygon E-3603).
- Remove plungers from two 30 mL syringes. Tape syringes together at top with regular tape. Attach female luers (45508-02) to syringes. Attach 18” tubing to luers.
- Attach 9” tubing to top port of two Lee company solenoid valves (LHDA1233215H), and 18” tubing from 30 mL syringes to middle ports. Tie each of 2” pieces in knot and slide one end over the bottom ports (Fig.3.1)
- Cut two 2” pieces of 18G stainless steel tubing with Dremel tool. Smooth at least one end for licking.
- Slide steel tubing into the two holes of the custom lickport holder. These holes may need to be reamed out with a #51 drill bit. Place tubes securely with ~ 1/2” sticking out of front end. Glue if necessary.
- Get two 10” wires (different color) and solder one end to steel tubing. Slide a piece of heat shrink over tubing and soldered wire. Heat with heat gun to shrink material and create tight fit. Crimp the other end of the wires to a female pin connector (Fig.3.2)
- Slide free ends of 9” plastic tubing over steel tubing on the heat shrink side.

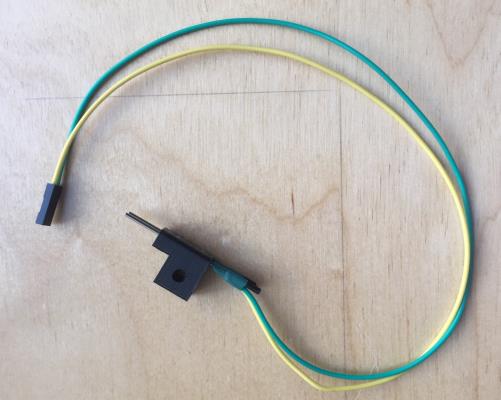
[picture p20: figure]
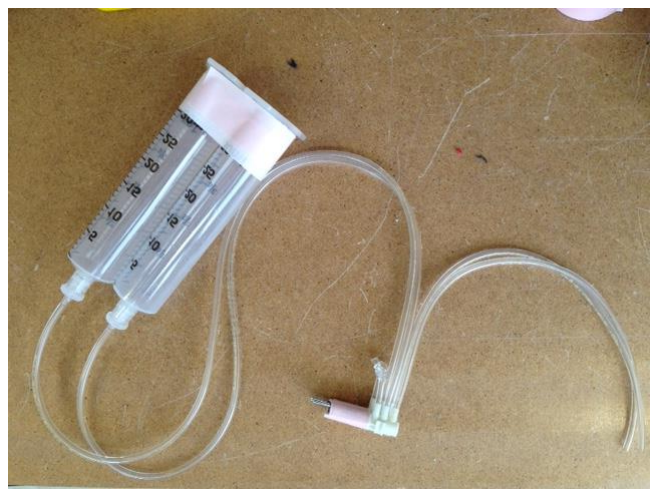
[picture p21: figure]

Fig. 3.1 | Fig.3.2
- Get a 3D-printed switch holder and two mini toggle switches, one for left solenoid and one for right solenoid. Fix the switches to the holder (Fig.3.3).
- Get five cables of 24”. Solder these 5 cables to the switches’ pin1, pin2 and pin3 accordingly as shown in the picture (Fig.3.4, Fig.3.5).
- Label “Flush” on the front panel of the switch holder to indicate the direction in which the switch is toggled to Pin1.

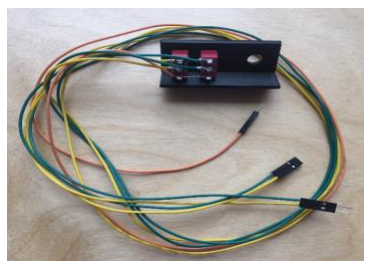
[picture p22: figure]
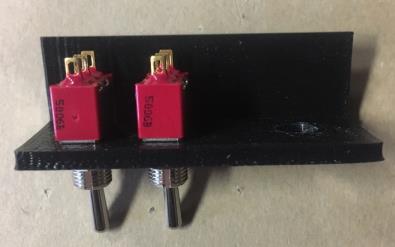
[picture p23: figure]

Fig. 3.3 | Fig. 3.4 | Fig. 3.5

### 4. Weighting Stage and Home-cage

- Get 3D-printed parts WeightingStage_bottom and WeightingStage_top, a micro load cell (Phidgets, 100g), a piece of aluminum sheet (2.5”x1.25”x0.016”) and a flat ribbon cable of 20 cm with one end having 6-pin (2x3) female connector (Fig.4.1).
- Fix the load cell on the WeightingStage_bottom using two screws (M2.5x12mm) and nuts. Make sure the arrow on the load cell is downward.
- Strip two ends of a wire. Tape one end of the striped wire on the aluminum sheet by aluminum tape. Route the other end of the wire out of the hole of WeightingStage_top and then out of the hole of WeightingStage_bottom. Glue the aluminum sheet on top of WeightingStage_top and let the side with the wire attached facing down.
- Secure WeightingStage_top on the load cell using another two screws (M2.5x12 mm) and nuts (Fig.4.2).
- According to the connector pinout in Table1, solder the four wires from load cell and one wire from the aluminum sheet to the open end of the ribbon cable (Fig. 4.3).

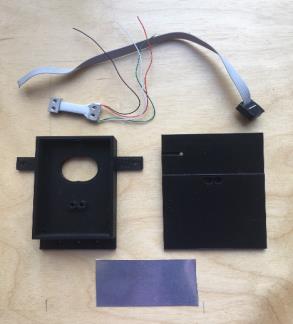
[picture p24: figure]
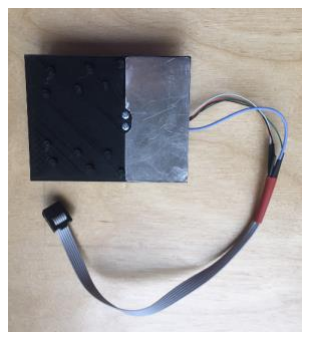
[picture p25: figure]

Fig. 4.1 | Fig. 4.2 | Fig. 4.3

Table 1. 6Pin (2x3) female connector Pinout

- Align the custom 3D-printed headport and the weighting stage assembled above against one side of the home-cage. According to the positions of the headport, drill two holes (7 mm) and one opening (30mm x 30mm). The headport should be attached to the home-cage such that the lower edge of the home-cage opening is trimmed with the weighting stage and the lower edge of the headport opening is a bit higher than the weighting stage (Fig.4.4).
- Drill a small opening (~15mm x 10mm) on the lower side of the home-cage to allow the ribbon cable connector (2x3 female connector) of the weighting stage go through.
- Align the weighting stage on the floor of the home-cage, centered around the opening. Mark the mounting locations and drill four threaded holes (4-40) on the floor. Fix the weighting stage to the threaded holes using size 4-40 screws (Fig.4.5).
Connector Pin# | Weighting Stage Wire
Pin 4 | AL Sheet
Pin 2 | RED
Pin 5 | BLACK
Pin 3 | WHITE
Pin 1 | GREEN

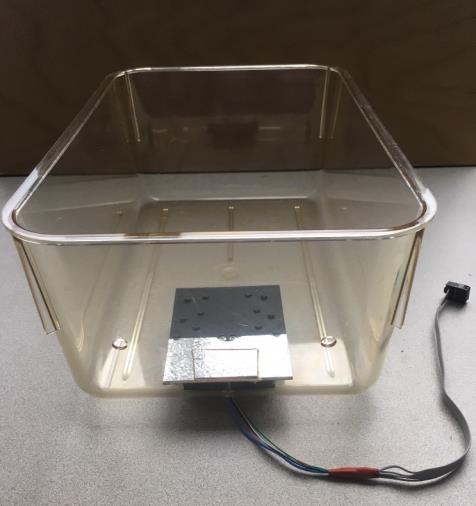
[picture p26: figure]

Fig.4.4 | Fig.4.5

### 5. Headport

### 5.1. Apply aluminum tape on the headport (Fig. 5.1):

- Apply aluminum tape on the floor of the headport opening and route it to the side of the headport by another piece of aluminum tape.
- Get a wire, strip two ends. Attach one end of the wire to the aluminum tape on the side of the headport and the other end of the wire will be soldered to the Headport ribbon cable.

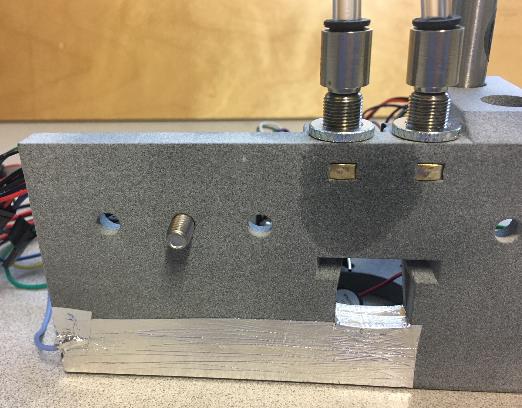
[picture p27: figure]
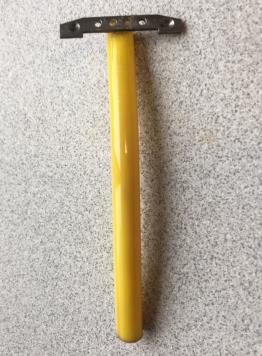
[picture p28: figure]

Fig. 5.1 | Fig.5.2

### 5.2. Set up switches (Fig.5.4):

- Get two snap action switches (D429-R1ML-G2) and four screws (M3x25mm) and nuts (Fig.5.3).
- Bend the first 3 mm of the switch lever outward to form a 90-degree angle.
- Fix the two switches on each side of the switch holder in the headport with the screws and nuts. Adjust the position to make sure the switches can be triggered only when the headbar (Fig.5.2) reaches the end of the headbar track of the headport.
- Connect pin1 of the two switches by soldering a jump wire. Solder a wire to pin4 of each switch and a wire to pin1 of one switch. These wires are with the other end free and to be soldered to the Headport ribbon cable.

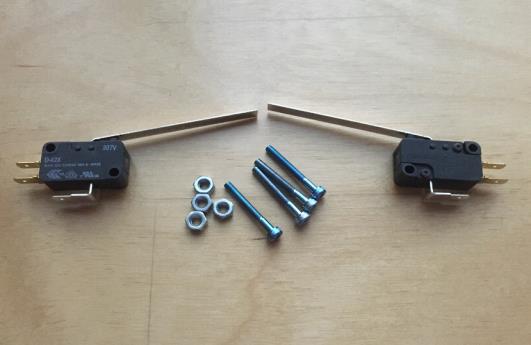
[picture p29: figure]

Fig.5.3 | Fig.5.4

### 5.3. Set up motors (Fig.5.5, Fig.5.6):

- Get one 50mm and one 30mm stroke motor (Actuonix, L12).
- Get one 3D-printed motor holder and thread the holes with 6-32 and 8-32 tap. Fix the
| 50mm motor at the tip of the 30mm motor in an orthogonal way using the 3D-printed holder with 6-32 x ¼” screws and 8-32 x ½” screw.
- Fix the lickport holder at the tip of 50mm motor using one screw (M4x25mm) and three nuts.
- Thread the two holes located at the lower right side of the headport floor using 6-32
| tap. Fix the motors on the headport floor using a bracket set which is came with the motor and 6-32 x 3/8” screws. Be sure to put a thin washer under the bracket to adjust the gap between the motor and the headport floor.
- From each motor, take red, black and blue wires and put them together into a 1x3 pin
| connector housing to be connected to the Headport ribbon cable.

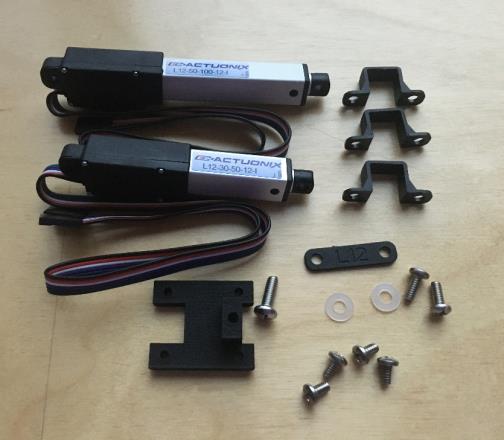
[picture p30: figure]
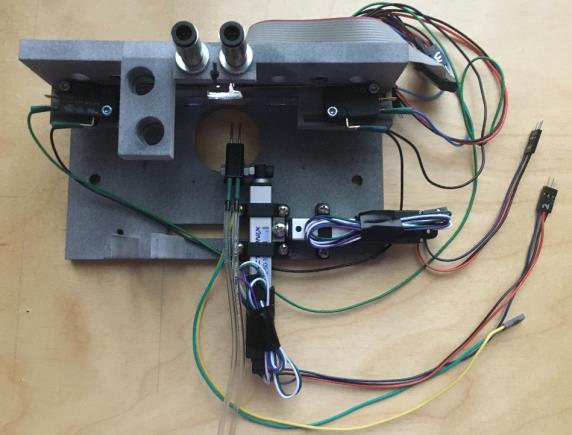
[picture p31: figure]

Fig.5.5 | Fig.5.6

### 5.4. Set up head-fixation pistons (Fig.5.7):

- Get two ¼’ OD Air Cylinder Pistons (McMaster, 6604K11) (with hex nuts). Grind the hex nuts outer shape to match the headport with Dremel.
- Insert two shaped hex nuts in the headport, screw the pistons in the piston holes of the headport and fix them with two Panel Nuts (McMaster, 5601396540).

- Screw two Push-in-Fitting connectors (McMaster, 5779K246) in the air inlet holes of the pistons.

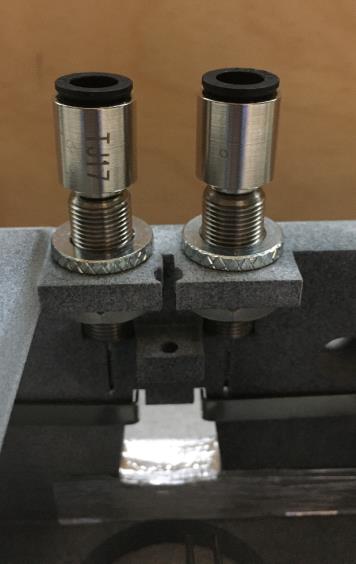
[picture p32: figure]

Fig.5.7

### 5.5. Set up pole mechanism (Fig.5.8, Fig.5.9):

- Get one Air Cylinder Pistons (McMaster, 6498K999). Insert the piston into the pole holder of the headport and screw one hex nut (10-32) on the rod of the piston until flush.
- Get one 3D printed pole and one 30mm stroke motor (Actuonix, L12-30). Insert the pole into the hole at the tip of motor. Take red, black, blue and purple wires from the motor and put them together into a 1x4 pin connector housing to be connected to the Headport ribbon cable.
- Fix the motor at the end of the piston with 3D printed bracket. Screw two hex nuts (3/8”-24) at the end until flush.
- Screw one Push-in-Fitting connectors (McMaster, 5779K246) in the air inlet holes of the pistons.

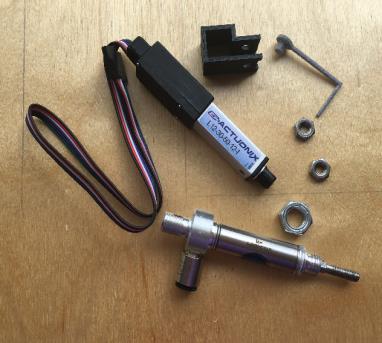
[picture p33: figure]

Fig.5.8 | Fig.5.9

### 5.6. Set up Piezo Buzzer (Fig.5.10)

- Get a Piezo Buzzer (490-CPE-160) and a cable with one end free and one end pre-crimped. Solder the free end of the cable to the Buzzer and have the other end ready to be connected to the headport ribbon cable. Fix the buzzer on the Headport floor.

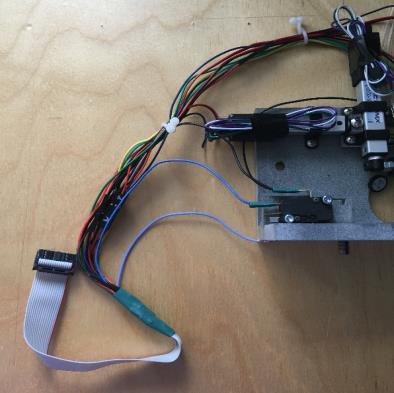
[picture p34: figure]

Fig.5.10 | Fig.5.11

### 5.7. Built the headport ribbon cable

- Get a flat Ribbon cable of 20cm with one end having 16Pin (2x8) female connector and the other end free.
- According to the connector pinout in Table2, solder and connect all the electric components located at the headport to the headport ribbon cable (Fig.5.11).

Table2. 16Pin (2x8) female connector Pinout:

Connector Pin# | Headport Electric Components Wires
Pin 1,3,5,16 | NC
Pin 9 | Piezo Buzzer + (Red)
Pin 11 | Switch L (pin4)
Pin 13 | Switch R (pin 4)
Pin 15 | Motor LR/FB/Pole GND (Black), Switch Com(pin1), Piezo Buzzer- (Black)
Pin 2 | Motor LR/FB/Pole Power (+12v, Red)
Pin 4 | Motor LR Voltage Input (Blue)
Pin 6 | Motor FB Voltage Input (Blue)
Pin 7 | Motor Pole Position Feedback (Purple)
Pin 8 | Motor Pole Voltage Input (Blue)
Pin 10 | Lickport Right
Pin 12 | Lickport Left
Pin 14 | Headport AL Tape

### 6. Pneumatics

- Attach a push-in-fit (QSM-M7-6-I) in the exhaust hole of the 3/2-way solenoid valve (hole no. 3). Connect it to a flow control valve (GRLA-1/8-QS-6-RS-D) using 6-mm tubing (Freelin-Wade, 1E-158-08)
- Get another flow control valve, attach a female push-in-fit (QSF-1/8-6-B) on the threaded port.
- Connect all the pneumatic parts using 6-mm tubing according to Fig.6.1.
- Attach a power/control cable (SIM-M12-5GD-2,5-PU) to the analog pressure regulator

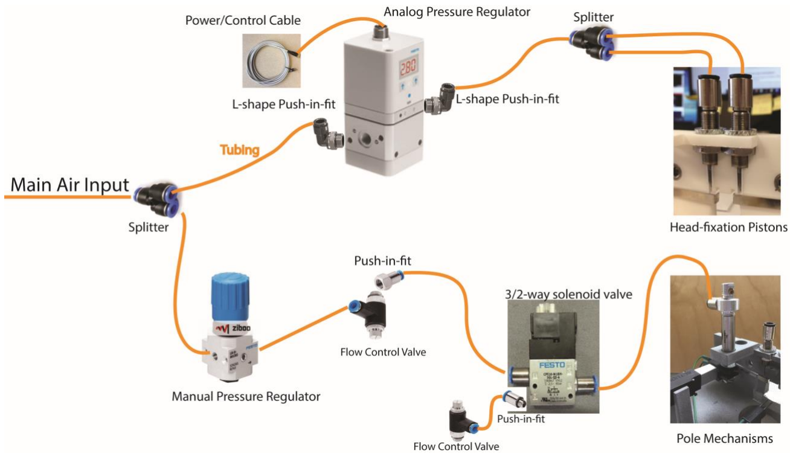
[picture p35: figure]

Fig. 6.1

### 7. Circuit and Assembly

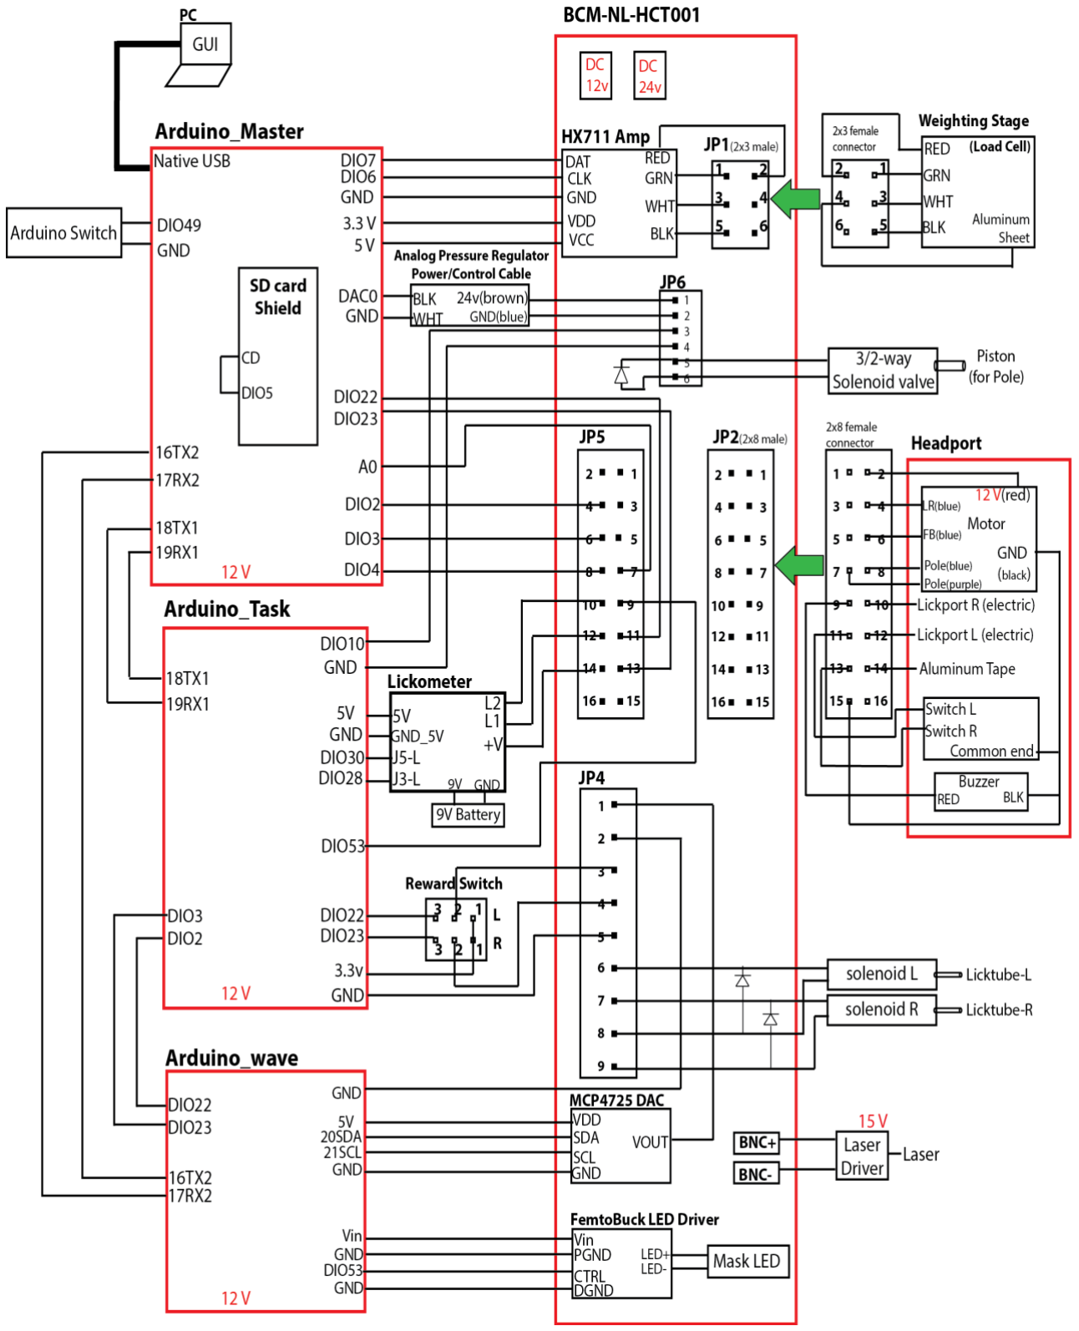
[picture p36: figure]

Fig.7.1

- Connect the electric circuit according to the above diagram Fig.7.1. The components in the circuit can be located at Fig.2.1, Fig.2.2, Fig.2.3 and Fig.3.4 accordingly. Fig.7.2 shows the completed circuit connection.

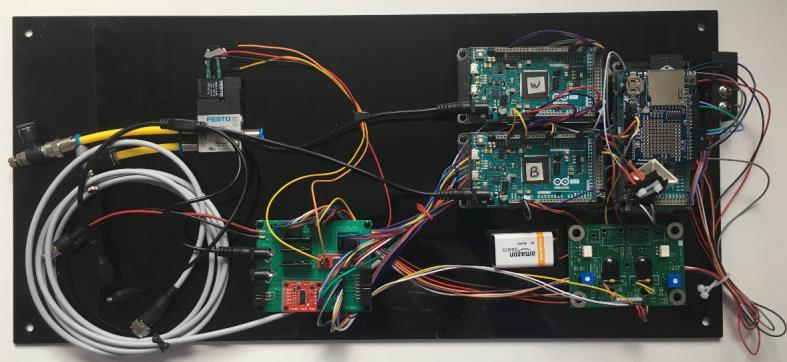
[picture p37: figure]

Fig. 7.2

- Use a 4-way Barrel Jack Splitter (Mouser, 485-1352) to connect together 12v power input ports on the three Arduino boards and BCM-NL-HCT001 board, and then connect the Splitter to a 12v AC/DC wall mount Adapter.
- Mount the Lee solenoids (Fig.7.3), reward switches (Fig.7.4) and Arduino switch (Fig.7.5) on the enclosure frame (Fig.7.6).

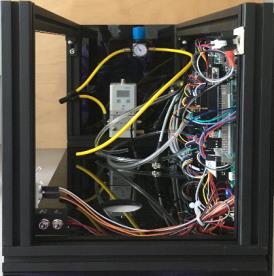
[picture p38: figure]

Fig.7.3 | Fig.7.4 | Fig.7.5 | Fig.7.6
- Table3 shows input/output of wires/pipes for the Automated Home-cage System after assembly.

Table3. Home-cage I/O
| Item Name | Function
Input | 12v AC/DC wall mount Adapter | Provide 12v power for Arduinos, motors and Lee solenoids
| 24v AC/DC wall mount Adapter | Provide 24v power for 3/2-way solenoid valve and analog pressure regulator
| USB 2.0 to Micro B Cable | Connect Arduino_Master to PC
| Plastic tube | Provide Air supply (4-bar) to Home-cage
Output | BNC Cable | Send voltages (0-5 V) to control Laser

### 8. Prepare Computer

The following software should be installed to the computer for testing and operating the Automated Home-cage System:
- Download the latest version of MATLAB from https://www.mathworks.com. After installed it, do the following steps to adjust Java Heap Memory to be half of the full Java Heap Size:
- Start MATLAB.
- On the Home tab, in the Environment section, click Preferences. Select MATLAB > General > Java Heap Memory.
- Select a Java heap size value using the slider or spin box.
- Click OK.
- Restart MATLAB.
- Download the Serial/TCP Terminal (realterm.exe) from https://sourceforge.net/projects/realterm/files/Realterm/
- Download the latest version of the Arduino IDE from https://www.arduino.cc. After installed it, with the Arduino plugged into a USB port, start up the IDE and make sure that the correct board name/version and COM port appears under the Tools menu.
- The COM port can be seen in the Windows Device Manager.
- A support package for Arduino DUE needs to be downloaded via the IDE:
- Click the menu item Tools → Board → Boards Manager.
- Search ‘due’ and find Arduino Due package.
- Click on the Install button that appears.
- Copy all the files in the folder “\Arduino programs\Tactile delayed response task\Library\” to the PC folder:\Program Files (x86)\Arduino\libraries\”.
- To upload an Arduino program to Arduino board via the IDE, do the following steps:
- Connect a USB cable from PC to the Native USB of the Arduino board.
- Click the menu item File → Open, select the program.
- Click the menu item Tools → Board, select the correct Arduino port
- Click the menu item Tools → Port, select the correct COM port.
- Click the button Upload.

### 9. Testing Procedure

### 9.1. SD Card

- Insert a battery (CR1220) to SD card shield.
- Copy all the files in the folder “\Test\final config files\” to a SD card.
- Insert the SD card to SD card shield.

### 9.2. On-board Date/Time Correction

- Upload “\Test\correctTime\correctTime.ino” to Arduino_Master board.
- After upload is done, run Realterm.exe on PC to receive Date/Time info from Arduino_Master board. The current Date/Time should be read on the Realterm display window.
- Do not reset Arduino when this step is done.

### 9.3. Weight Calibration

- Do not reset Arduino from last step.
- Upload “\Test\Weight_Calibration\Weight_Calibration.ino” to Arduino_ Master board and run Realterm.exe on PC to receive weight info.

- After readings start, place an object with known weight on the weighting stage. The reading on the Realterm display window should be roughly matched to the weight. Adjust the calibration_factor if the reading is not matched.
- Set the correct calibration_factor in the program “\Arduino programs\XXX task\ Arduino_ Master\Arduino_Master.ino”.

### 9.4. Upload Arduino program

In the folder “\Arduino programs\Tactile delayed response task\”:
- Upload “\Arduino_Wave\Arduino_Wave.ino” to the Arduino_Wave board.
- Upload “\ Arduino_Task\Arduino_Task.ino” to the Arduino_Task board.
- Upload “\ Arduino_ Master\Arduino_Master.ino’”to the Arduino_ Master board.

### 9.5. Air/Power supply

- Supply the plastic tube of the Automated Home-cage System with the compressed air 4 bars.
- Adjust the manual pressure regulator (Fig.2.1) to 2 bars and check if there is air leaking.
- Power up the Automated Home-cage System with 12V and 24V adapters.
- Connect the USB cable from the Native USB Port of the Arduino_Master board to PC.

### 9.6. Test motors and adjust motor position

- Run “\Matlab GUI\homecage_gui.m program in MATLAB and the HomeCage GUI shows up as Fig.9.1.
- In HomeCage GUI, choose a cage and open the corresponding COM.
- In Control Panel of HomeCage GUI, choose the above cage, input a value (0-255) and click “Move & Set” to see if the corresponding motor moves by the expected distance.
- Move the LR motor to the initial position (70 by default), loose the bracket which holds the LR motor, adjust the location of the LR motor so that the lickport is roughly at the center of the head port.
- Move the FB motor to the final position (30 by default), loose the bracket which holds the FB motor, adjust the location of the FB motor so that the tip of the lickport is about 14 mm from the wall of the headport. And then move the FB motor to the position 130, the tip of the lickport should just touch the wall.

### 9.7. Test Tare and Calibration function

- Make sure nothing is on the weighting stage and click Tare button in HomeCage GUI.
- Put an object with known weight W (g) on the weighting stage and input the weight value W in the text field of “Known_W”, and then click Calibration button.
- Click Read button, the text field of Weight should show a value close to W.
- Take off the object from the weighting stage and Click Read button again, the text field of Weight should show a value close to Zero.

### 9.8. Test the reward solenoid valves

- Fill the water reservoir with water.
- Toggle the reward switch to the “Flush” side to turn on the solenoid valve. The water should flow out of the water reservoir, fill up the whole tubing and then flow out of the lickport.
- Toggle the reward switch to the other side. When turn on the Arduino switch, A drop of water should come out of both lickport tubes.
- Click Set&Reward button in Homecage GUI, and a drop of water should also come out of both lickport tubes.

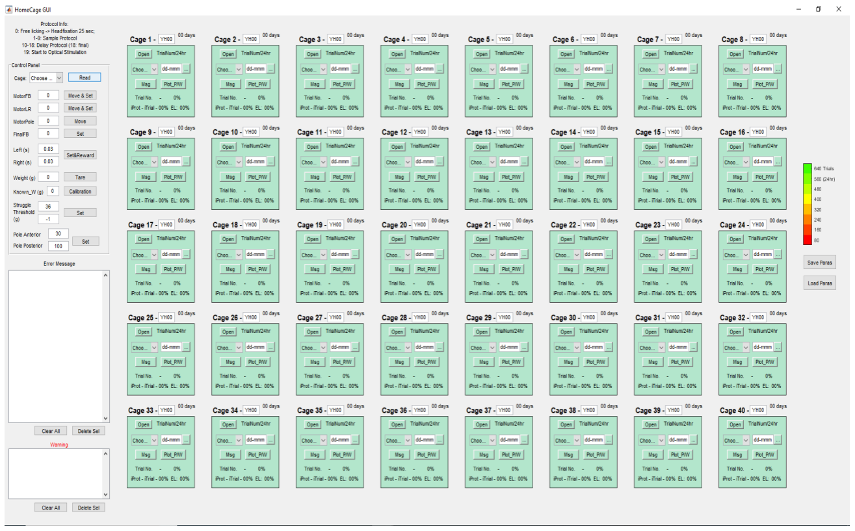
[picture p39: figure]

Fig.9.1

### 9.9. Test the lickometer board (Fig.9.2)

- The two Trimmer Resistors (R10/R21) on the lickometer board should be turned to the maximum value.
- The two capacitors on the lickometer board should be 0.47uf.
- Measure the voltage between the left and right pins in J3/J5 of the lickometer board, the resting voltage is around 0.3v, and the voltage goes up to around 3.8v when you connect the left/right lickport to the aluminum tape on the headport by your hand.
- Connect both J3 and J5 to an oscilloscope (left pin to probe and right pin to ground), touch the lickport by your hand, and check if there is any crosstalk between the two lickport tubes. Adjust R10/R21 and change the capacitors if necessary.

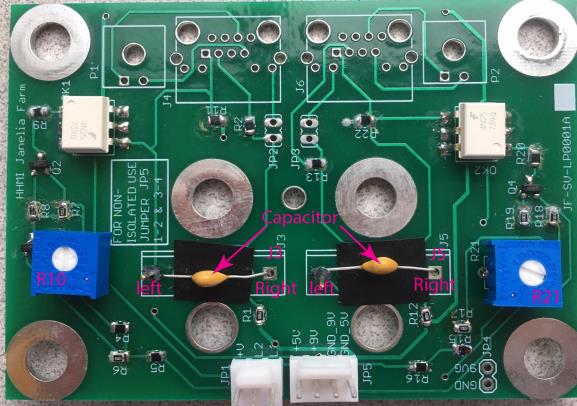
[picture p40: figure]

Fig.9.2

### 9.10. Test the trial sequence

### 9.10.1. Trial sequence

- With the SD card having the final config files, turn on the Arduino switch and trigger the two switches in the headport by the headbar. The trial runs in the following sequence:
1) Pistons for head-fixation comes down.
2) Motor for pole moves either forward or backward depending on the trial type.
3) Masking LED turns on and flashes.
4) Piston for pole comes down and stays down for about 1.3s.
5) Piston for pole comes up.
6) Piezo Buzzer makes a go cue sound.
7) Masking LED off.
Trials repeat the above sequence (1-7) until the head fixation is timeout (~60s), and then the Pistons for head-fixation comes up. Each trial takes about 6s.

### 9.10.2. Checking List

During a trial, check the functionality of the following items:
- Pistons for head-fixation: coming down and retracting smoothly, fixation (staying down) for ~60s.
- Piston for pole: coming down and retracting smoothly. Adjust the flow control valves if necessary.
- Motor for pole: moving forward and backward smoothly.
- Masking LED: flashing during the whole trial (~5 sec).
- Lickports: the left and right lickports can be detected separately and correctly. Depending on the trial type, a drop of water should come out of the left/right lickport if the corresponding lickport is connected to the aluminum tape on headport/weighting stage by your hands right after the go cue sound is heard in each trial.
- Weighting stage: during head-fixation, press or lift the weighting stage lightly, the pistons for head-fixation should be released.

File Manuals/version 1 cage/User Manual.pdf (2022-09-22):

## Automated Home-cage System User Manual

The Automated Home-cage System is a fully autonomous mouse behavioral and optogenetic experiment system. This manual will guide you through the initial check and installation of your system. It also describes operation, maintenance, and diagnostic procedures of your system.

### 1. Hardware Checklist

- The Automated Home-cage System is a fully enclosed system as shown in Fig.1.1.

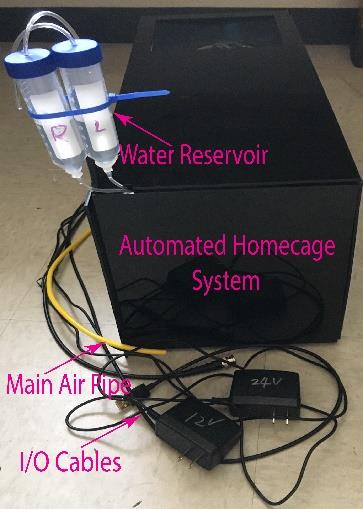
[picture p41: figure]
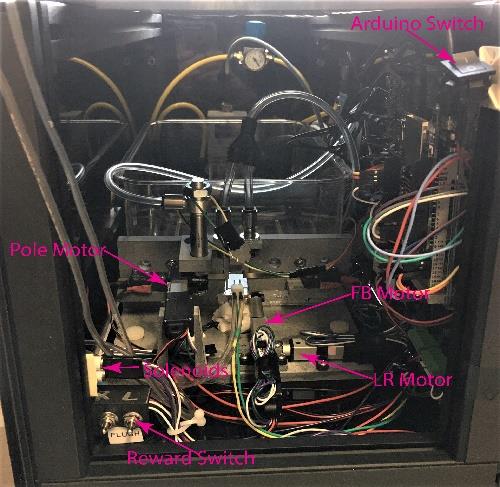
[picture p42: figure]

Fig.1.1 | Fig.1.2
- There are four electric cables and one plastic tube come out from the left side of the enclosure. Refer to table1 for their specifications.
Table1. Home-cage I/O
| Item Name | Function
Input | 12v AC/DC wall mount Adapter | Provide 12v power for Arduinos, motors and Lee solenoids
| 24v AC/DC wall mount Adapter | Provide 24v power for 3/2-way solenoid valve and analog pressure regulator
| USB 2.0 to Micro B Cable | Connect Arduino_Master to PC
| Plastic tube | Provide Air supply (4-bar) to Home-cage
Output | BNC Cable | Send voltages (0-5 V) to control Laser
- The water reservoir, the Arduino switch, the reward switches, and the solenoids are located at the front frame of the enclosure (Fig.1.2).
- All the circuit boards are mounted on the right side of the enclosure (Fig.1.3).

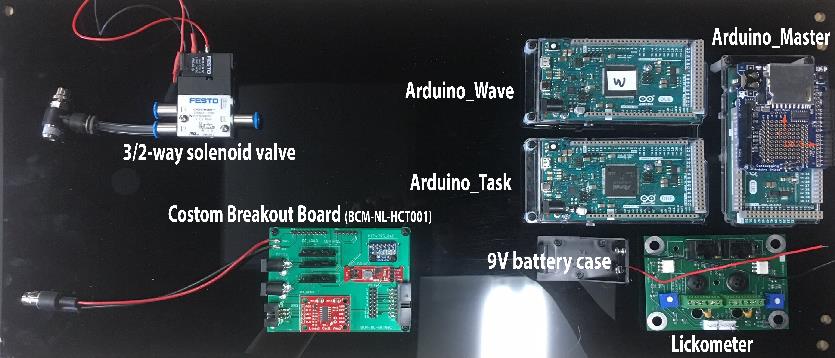
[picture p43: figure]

Fig.1.3

- The Home-cage and the Headport are fixed on the floor of the enclosure (Fig.1.4).

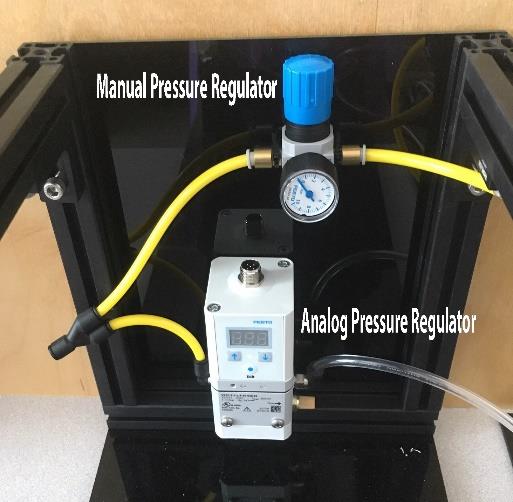
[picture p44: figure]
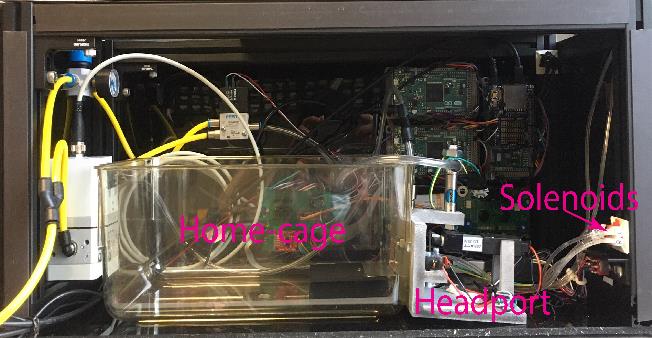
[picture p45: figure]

Fig.1.4 | Fig.1.5
- Two pressure regulators are mounted on the back side of the enclosure (Fig.1.5).

### 2. Software installation

- Download the latest version of MATLAB from https://www.mathworks.com. After installed it, do the following steps to adjust Java Heap Memory to be half of the full Java Heap Size:
- Start MATLAB.
- | On the Home tab, in the Environment section, click | Preferences. Select
| MATLAB > General > Java Heap Memory.
- Select a Java heap size value using the slider or spin box.
- Click OK.
- Restart MATLAB.
- Download the latest version of the Arduino IDE from https://www.arduino.cc. After installed it, with the Arduino plugged into a USB port, start up the IDE and make sure that the correct board name/version and COM port appears under the Tools menu.
- The COM port can be seen in the Windows Device Manager.
- A support package for Arduino DUE needs to be downloaded via the IDE:
- Click the menu item Tools → Board → Boards Manager.
| • Search ‘due’ and find Arduino Due package. • Click on the Install button that appears.
- Copy all the files in the folder “\Arduino programs\XXX task\Library\” to the PC
| folder:\Program Files (x86)\Arduino\libraries\”.
- To upload an Arduino program to Arduino board via the IDE, do the following
| steps:
- Connect a USB cable from PC to the Native USB Port of the Arduino
| board
- Click the menu item File → Open, select the program.
- Click the menu item Tools → Board, select the Native USB port.
- Click the menu item Tools → Port, select the correct COM port.
| • Click the button Upload.

- Upload Arduino program to Arduino board according to the task. In the folder “\Arduino programs\XXX task\”:
- Upload “\Arduino_Wave\Arduino_Wave.ino” to the Arduino_Wave board.
- Upload “\Arduino_Task\Arduino_Task.ino” to the Arduino_Task board.
- Upload “\ Arduino_ Master \Arduino_Master.ino” to the Arduino_ Master board.

### 3. HomeCage GUI

HomeCage GUI is created for user to easily interface with the Arduino_Master board during experiment. To use HomeCage GUI, copy folder “\Matlab GUI\” to the PC, connect the system to the PC and run “\Matlab GUI\homecage_gui.m” program in MATLAB. HomeCage GUI shows up as Fig.3.1. The main functions are described as follows:
3.1.Cage block
- Set the mouse name, the experiment starting date and the COM port for the corresponding cage. Click open button to communicate to Arduino_Master board.
- Click Msg to get the experiment information (message) in last 24 hours.
- Click Plot_ P/W to plot the mouse behavior data in last 24 hours.
- The last 24 hours data/message stored in the local PC will be clear once click close button, disconnect the USB cable from PC, or Arduino_Master board is reset. 3.2.Control panel
- Choose the cage that you want to interface with.
- Click read to get the on-line motor positions and mouse weight and show them in the corresponding text fields.
- Set a value in text field of MotorFB, click Move& Set to move the FB motor and set its position value in the Arduino code.
- Set a value in text field of MotorLR, click Move& Set to move the LR motor and set its position value in the Arduino code.
- Set a value in text field of MotorPole, click Move to move the Pole motor.
- Set a value in text field of FinalFB, click Set to set the final position value of the FB motor in the Arduino code.
- Set a value in text field of Left/Right, click Set&Reward to set the reward size and a drop of water comes out of lickport.
- Tare and Calibration is used to get the offset and scale of the weighting stage, set them in the Arduino code and also save to the SD card on the Arduino_Master board.
- Set a value in text fields of Struggle Threshold, click Set to set the range of the mouse struggle threshold in the Arduino code.
- Set a value in text field of Pole Anterior/Posterior, click Set to set the anterior and posterior position value of the Pole motor in the Arduino code.
3.3.Save Paras and Load Paras Button
- Click Save Paras or Load Paras to save or load the settings of the mouse name, the experiment starting date and the COM port number for all the cages.

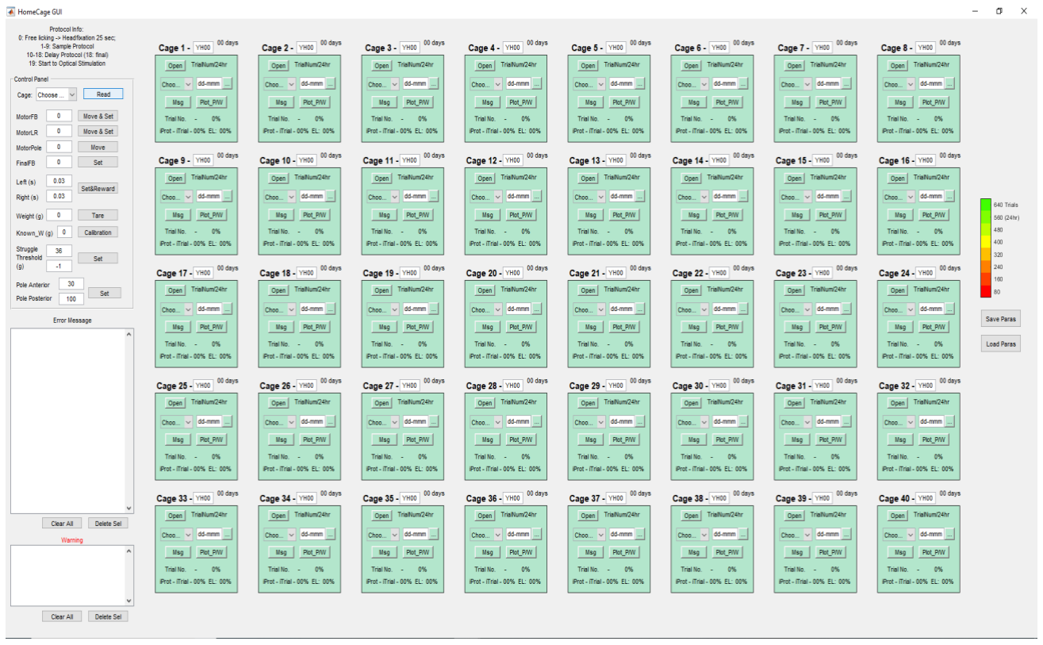
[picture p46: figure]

Fig.3.1

### 4. Operation Procedures

1. Move the Automated Home-cage system to the workstation where there are the compressed air supply and the power outlet accessible.
2. Connect the plastic tube from the system to the compressed air supply (4 bars).
3. Adjust the manual pressure regulator to 2 bars and check if there is air leaking.
4. Make sure the Arduino switch is switched to “OFF”.
5. Copy the two initial parameter files (PARAF.TXT and PARAS.TXT) in the folder “\Arduino programs\XXX task\initial config files\” to a blank SD card and insert the SD Card into the SD card shield on the Arduino_Master board.
6. Adjust the height of the lickport to make sure it is higher than the bottom edge of the headport opening.
7. Power up the 12V and 24V adapter and then connect Arduino_Master board to USB hub via USB cable.
8. The lickport will be moved into the headport opening.
9. Run “\Matlab GUI\homecage_gui.m” program in MATLAB. Set the mouse name, start date and the com port in the corresponding cage block of the HomeCage GUI. Click open button to start receiving data from Arduino_Master board.
10. Make sure nothing is on the weighting stage and click Tare button to zero the weighting stage and get the offset of the weighting stage.
11. Put an object with known weight W (g) on the weighting stage, input the weight value W in the text field of “Known_W”, and click Calibration button to get the Scale of the weighting stage.

12. Click Read button, the text field of Weight should show a value close to W. Take off the object from the weighting stage and click Read button again, the text field of Weight should show a value close to Zero.
13. After toggled the Arduino switch to “ON”, trial 1 starts and the pole drops down. Touching the lickport by your hand will trigger another trial.
14. Put bedding, food, hiding tube into the home-cage.
15. Put the mouse into the home-cage.
16. Cover the home-cage with the lid and the system enclosure with the top panel.
17. Repeat the above steps if you have more cages. Click Save Paras button to save the cage setting parameters once you finished setting up the cages.

### 5. Maintenance

5.1.Connect to PC
- if you want to use HomeCage GUI to interface with Arduino_Master board and check mouse behavior while experiment is running, the Automated Home-cage System needs to connect to a PC, even though it can fully function without connecting to a PC.
- In the event that MATLAB crushes while experiment is running, close MATLAB, and make sure that the Automated Home-cage Systems are still running fine. Restart MATLAB and run HomeCage GUI again.
5.2.SD Card
- For a new mouse, copy the two initial parameter files (PARAF.TXT and PARAS.TXT) in the folder “\Arduino programs\XXX task\initial config files\” to a blank SD card and start the experiment. While the trials are going on, there are six files stored in the SD Card. Refer to “\example data\README.txt” for the detail explanations of these files.
- When putting a different mouse to the same cage, make sure to change the SD card for the particular mouse.
- When changing SD Card, i.e., pulling one out from and pushing the other one into the SD Card shield, be sure to turn off the Arduino switch.
5.3.Weighting Stage Initialization
- When click Tare and Calibration button, the program performs the weighting stage initialization and saves the offset and scale of the weighting stage to the file PARAF.TXT in SD card. You must perform Tare and Calibration in the following circumstances:
- Using a new cage.
- Using a SD card which is new to the particular cage.
- After replacing the load cell for the weighting stage. 5.4.Weighting Stage Routine Check
- In order to get the mouse weight accurately while the experiment is going on, it is important to check the weighting stage routinely via HomeCage GUI:
- Make sure nothing is on the weighting stage and click Tare button to zero the weighting stage.
- Click Read button, the text field of Weight should show a value close to zero.

- Put an object with known weight W (g) on the weighting stage and click Read button again, the text field of Weight should show a value close to W (g).
5.5.Reward Solenoid Routine Check
- Use Set&Reward button in Homecage GUI to set the reward size for both left and right lickport. Make sure the actual reward drops are roughly equal on both sides.
- Check the reward size routinely. If noticing a much smaller reward size while the experiment is going, flush the water line first to see if the reward size is back to normal. If not, replace with a new solenoid.

### 5.6. Pole Motor

- Too much pole activity can cause the motor malfunction. when the malfunction happened, a warning message appears in Warning box of HomeCage GUI indicating which cage’s pole motor is malfunction and the experiment pauses.
- In the case the warning message appears, be sure to verify if the pole motor is malfunction. Set a value in text field of MotorPole and click Move to move the Pole motor. If the pole motor does not move, carry on the following steps:
- Turn off the Arduino switch.
- Refer to section 5.5 of “Automated Home-cage System construction Manual” and replace the pole motor.
- Open “PARAS.TXT” file in the SD card, change parameter “is_motor_ok” from 0 to 1 and save.
- Insert the SD card back to the SD card shield.
- Turn on the Arduino switch to continue the experiment.
5.7.Arduino Board Reset
- In general, there is no need to reset the Arduino boards manually, i.e., by pushing the reset button at the Arduino board. When power up, the three of Arduino boards reset and handshake with each other automatically.
- In the event that Arduino_Master board hangs while experiment is running, the embedded watchdog timer will reset Arduino_Master board automatically, and the experiment should continue without issues.
- In case you have to reset the Arduino boards manually, be sure to reset Arduino_Wave board and Arduino_Task board first, and then reset Arduino_Master board.
5.8.Communication between Arduino Boards
- When the communication between Arduino_Master board and Arduino_Task board has issue, a warning message (handshake failed) appears in Warning box of HomeCage GUI indicating which cage’s Arduino boards are handshake failed and the experiment pauses.
- In the case the warning message appears, carry on the following steps:
- Turn off the Arduino switch.
- Troubleshoot the issue.
- Reset Arduino_Master board. On HomeCage GUI, click open button on the corresponding cage, a message (handshake successful) should appear in Message box If the issue is fixed.
- Turn on the Arduino switch to continue the experiment.

5.9.Lickport Position
During Auto-training, check and adjust the Lickport position periodically:
- When the lickport retracts out of the headport, adjust its height to a bit higher than the bottom edge of headport opening (Fig.5.1) and make sure it is still at the center of the head port opening in left-right direction.
- When lickport reaches the final position, there is a one-time adjustment of the position to make sure the mouse can access both tubes of the lickport and the lickport is in the center roughly (Fig.5.2). The final FB motor position can be adjusted via the HomeCage GUI as described in section 3.

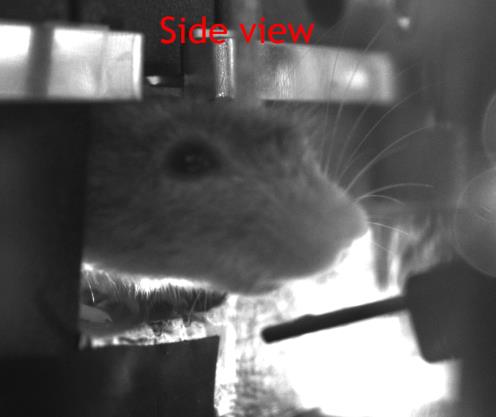
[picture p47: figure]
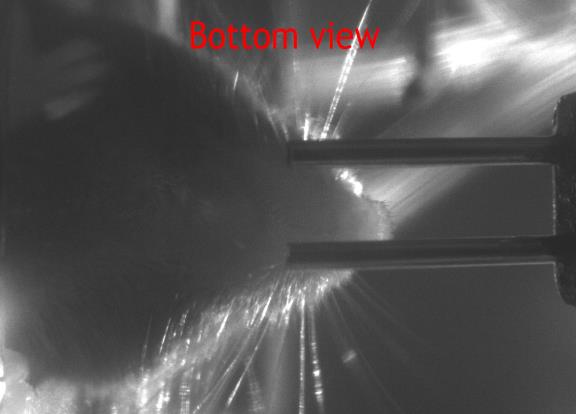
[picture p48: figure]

Fig.5.1 | Fig.5.2

### 5.10. Clean Home-cage

The home-cage can be detached from the system to be cleaned:
- Unscrew the two screws (inside home-cage) that fixes the home-cage with the headport.
- Detach the 6pin connector that connects weighting stage to the circuit board on the right side of the enclosure.
- When clean the home-cage, be sure to take a good care of the weighting stage (no
| hard press to the stage), the 6pin connector and the ribbon cable.

### 5.11. Power on/off

- In general, the system can be power on all the time.
- In the event you want to power off the system, follow the sequence: turn off the
| Arduino Switch, unplug 12V adapter and 24V adapter, unplug USB cable from PC,
turn off the air supply.
- In the event you want to power on the system, follow the sequence: turn on the air
| supply, plug in 12V adapter and 24V adapter, plug in USB cable from PC, turn on the
Arduino Switch.

### 5.12. Add/Modify protocol

To modify an existing protocol or add a new protocol, you should modify the existing states or create new states by editing the function “send_protocol_to_Bpod_and_Run()” in “\Arduino programs\XXX task\Arduino_Master\Arduino_Master.ino”.
- In function “send_protocol_to_Bpod_and_Run()”, modify/add new state using function “CreateState()”.
- The function ”CreateState()” constructs a state struct defined by the input
| arguments and returns a constructed state. There are 5 input arguments:

- Name: The name of the state.
- TimeOut: A float variable indicating the state timeout.
- nChangeConditions: The number of state transitions defined.
- StateChangeConditions: The pointer to the state transitions.
- nOutputActions: The number of output actions.
- Outputs: The pointer to the output actions.

### 6. Trouble Shooting

### 6.1. Mice do not enter trigger head fixation for extended period of time

6.1.1. Mouse cannot poke in the headport (Fig.6.1)
- Check the headbar position: anterior edge of headbar should line up with lambda suture; depressions face up.
- NO glue or dental cement should occlude either side of the headbar.
- Headbar position should be consistent from mouse to mouse.

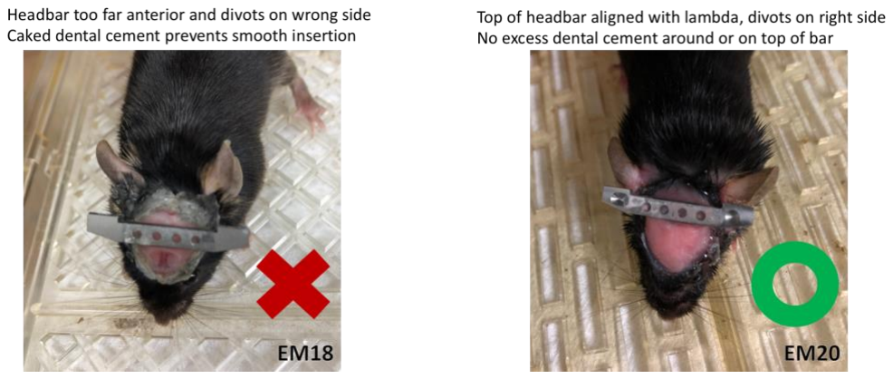
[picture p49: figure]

Fig.6.1.

6.1.2. Mouse cannot access the lickport because the lickport is far from mouse
- The lickport position needs to be adjusted, refer to section 5.8 for how/when to adjust the lickport position.
6.1.3. The program cannot detect licking when mouse licks
- Check if metal sheet on the weighting stage is electrically connected with the Lickometer to form a complete circuit. The resistance between metal sheet on the weighting stage and the aluminum tape on headport should be less 10 Ohm if the connection is good.
- Check if the 9v battery is good and the voltage is more than 8 Volt.
- The Lickometer may be malfunction, refer to section 9.9 of “Automated Homecage System construction Manual” for how to check Lickometer.

### 6.2. Mice do not advance in training for extended period of time

6.2.1. The pole does not drop down during the task
- The pole may be stuck. Increase the air pressure to 3-4 bar to let the pole drop down then go back to 2 bars as normal.
- Try manually press down the pole (together with the motor).

6.2.2. Reward could be running slow
- Check periodically that water is coming out and the flow on the two lickspouts is evenly.
- Check if there is any clog in tubes and solenoid. Clean the water lines if necessary.
- Check if the solenoid is malfunctioned.
6.2.3. The mouse triggers self-release too frequently.
- Make sure the mouse is not on the platform, and then click the Tare button in HomeCage GUI.
- Check if the top panel of the weighting stage is block by bedding or other stuff.
6.2.4. The pole motor is not firmly fixed at the end of the piston.
- Check if the screws are loosed or the 3D printed bracket is broken due to too much piston activity. This should be checked periodically.

### 7. Training data Example

- Fig.7 shows example learning curve of number of switch trigger (A), number of head-fixation (B), number of reward (C), weight (D) and histogram of number of re-extend of lickport (E). These data are from ~35 example mice and only first 10 days are showed to illustrate the trend.

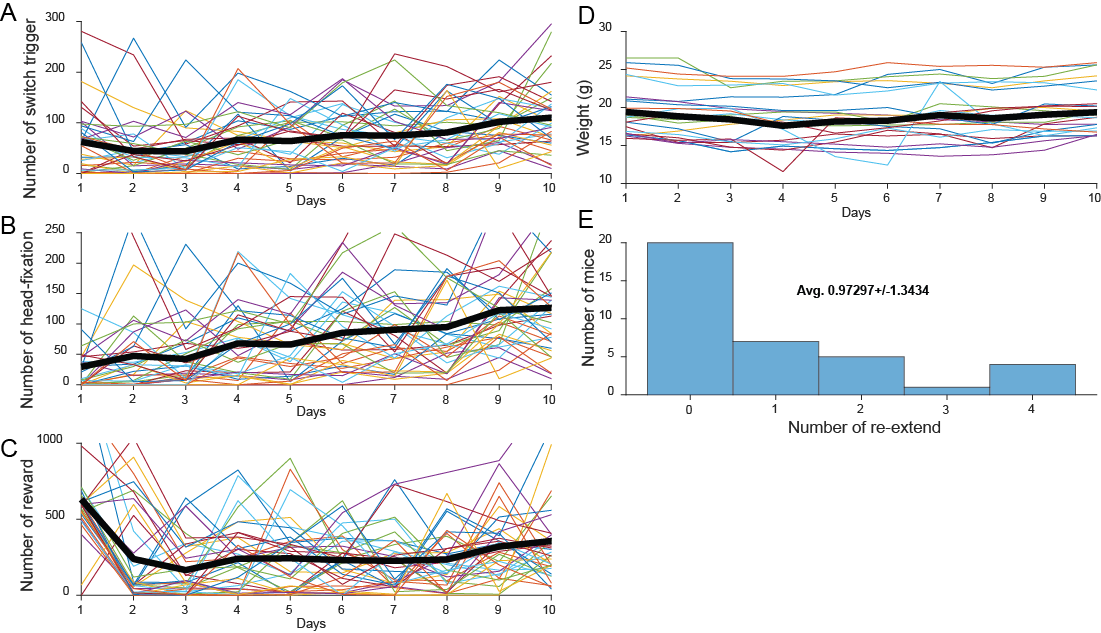
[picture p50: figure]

Fig.7

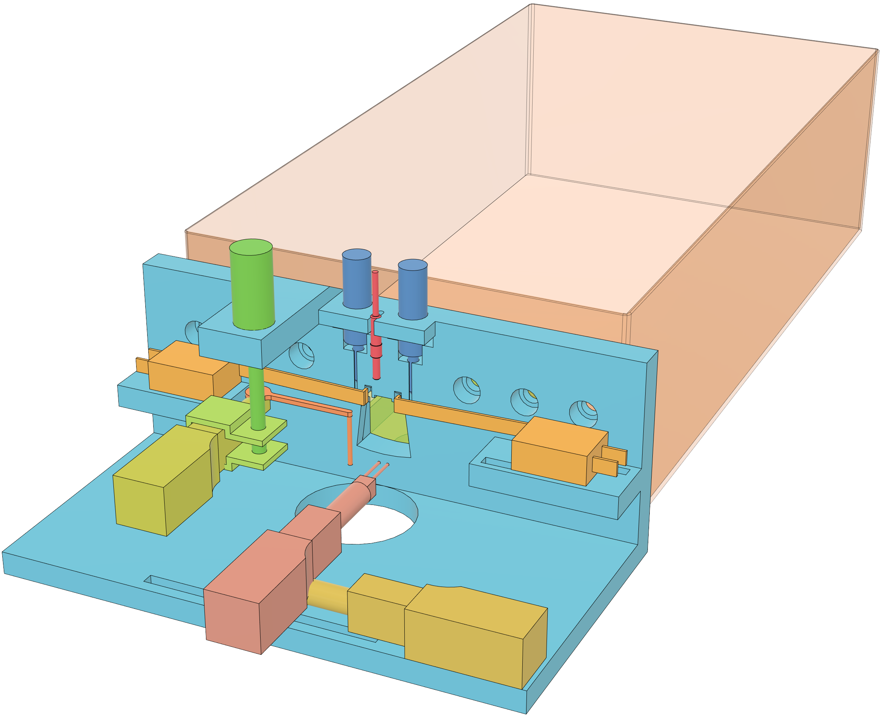
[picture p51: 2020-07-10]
Design files/media/Assemble v42.png

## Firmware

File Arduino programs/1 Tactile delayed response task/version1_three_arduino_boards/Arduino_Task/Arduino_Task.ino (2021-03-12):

/* by Yaoyao
  changes from the original version from Sanworks.
  1. the whole structure was changed to adapt the slow commnucation via serial1 (instead of SerialUSB),
    see https://sanworks.io/forum/showthread.php?tid=142
  2. All the Bpod communication with PC was shut down
  3. comment green/blue led pin; CHANGE updateStatusLED()
  4. ValveRegWrite() w/ reg => ValveWrite() w/ digitalwritedirect()
  5. comment SyncRegWrite()
  6. do not send back envent during running.
  7. pwm1: true pwm used for go cue, etc. pwm2-8: stay the same, i.e., analogwrite()
   also UpdatePWMOutputStates() only work on pwm2-8
   in setStateOutputs(), change pwm1 to true pwm

  ----------------------------------------------------------------------------

  This file is part of the Sanworks Bpod repository
  Copyright (C) 2016 Sanworks LLC, Sound Beach, New York, USA

  ----------------------------------------------------------------------------

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
*/
// Bpod Finite State Machine v 0.5
// Requires the DueTimer library from:
// https://github.com/ivanseidel/DueTimer
#include <DueTimer.h>
#include <SPI.h>
#include "pwm_lib.h" // pwm lib for go cue sound

byte FirmwareBuildVersion = 6;
//////////////////////////////
// Hardware mapping:        //
//////////////////////////////

//     8 Sensor/Valve/LED Ports
byte PortDigitalInputLines[8] = {28, 30, 32, 34, 36, 38, 40, 42};
byte PortPWMOutputLines[8] = {53, 8, 7, 6, 5, 4, 3, 2}; // pwm1: gocue; pwm2-8: digital
//PWMH0_PC3  // PWM_CH0 pin35
//PWMH1_PA19 // PWM_CH1 pin42
//PWMH2_PB14 // PWM_CH2 pin53
using namespace arduino_due::pwm_lib;
// for go cue sound
#define PWM_PERIOD_PIN_53 27000 //3.7khz    //28600 // 3.5 kHz        //10000 // 100 us, 10 kHz
#define PWM_DUTY_PIN_53   13500             //14300 // 50% duty
// defining pwm object using pin 35, pin PC3 mapped to pin 35 on the DUE
// this object uses PWM channel 0
pwm<pwm_pin::PWMH2_PB14> pwm_pin53;




byte PortAnalogInputLines[8] = {0, 1, 2, 3, 4, 5, 6, 7}; // not used!!!

//     wire
byte WireDigitalInputLines[4] = {35, 33, 31, 29};
byte WireDigitalOutputLines[4] = {43, 41, 39, 37};

//     SPI device latch pins
//byte ValveRegisterLatch = 22;
//byte SyncRegisterLatch = 23;
byte ValveDigitalOutputLines[2] = {22, 23};

//      Bnc
byte BncOutputLines[2] = {10, 11};
byte BncInputLines[2] = {24, 25};

//      Indicator
byte RedLEDPin = 13;
//byte GreenLEDPin = 14;
//byte BlueLEDPin = 12;


//////////////////////////////////
// Initialize system state vars: /
//////////////////////////////////

byte PortPWMOutputState[8] = {0}; // State of all 8 output lines (As 8-bit PWM value from 0-255 representing duty cycle. PWM cycles at 1KHZ)
byte PortValveOutputState = 0;   // State of all 8 valves
byte PortInputsEnabled[8] = {0}; // Enabled or disabled input reads of port IR lines
byte WireInputsEnabled[4] = {0}; // Enabled or disabled input reads of wire lines
boolean PortInputLineValue[8] = {0}; // Direct reads of digital values of IR beams
boolean PortInputLineOverride[8] = {0}; // set to 1 if user created a virtual input, to prevent hardware reads until user returns it to low
boolean PortInputLineLastKnownStatus[8] = {0}; // Last known status of IR beams
boolean BNCInputLineValue[2] = {0}; // Direct reads of BNC input lines
boolean BNCInputLineOverride[2] = {0}; // Set to 1 if user created a virtual BNC high event, to prevent hardware reads until user returns low
boolean BNCInputLineLastKnownStatus[2] = {0}; // Last known status of BNC input lines
boolean WireInputLineValue[4] = {0}; // Direct reads of Wire terminal input lines
boolean WireInputLineOverride[2] = {0}; // Set to 1 if user created a virtual wire high event, to prevent hardware reads until user returns low
boolean WireInputLineLastKnownStatus[4] = {0}; // Last known status of Wire terminal input lines
boolean MatrixFinished = false; // Has the system exited the matrix (final state)?
boolean MatrixAborted = false; // Has the user aborted the matrix before the final state?
boolean MeaningfulStateTimer = false; // Does this state's timer get us to another state when it expires?
int CurrentState = 1; // What state is the state machine currently in? (State 0 is the final state)
int NewState = 1;
byte state_visited[1024] = {};
uint16_t nTransition = 0;

byte CurrentEvent[10] = {0}; // What event code just happened and needs to be handled. Up to 10 can be acquired per 30us loop.
byte nCurrentEvents = 0; // Index of current event
byte SoftEvent = 0; // What soft event code just happened


//////////////////////////////////
// Initialize general use vars:  /
//////////////////////////////////

byte CommandByte = 0;  // Op code to specify handling of an incoming USB Serial message
byte VirtualEventTarget = 0; // Op code to specify which virtual event type (Port, BNC, etc)
byte VirtualEventData = 0; // State of target
int nWaves = 0; // number of scheduled waves registered
byte CurrentWave = 0; // Scheduled wave currently in use
byte LowByte = 0; // LowByte through FourthByte are used for reading bytes that will be combined to 16 and 32 bit integers
byte SecondByte = 0;
byte ThirdByte = 0;
byte FourthByte = 0;
byte Byte1 = 0;
byte Byte2 = 0;
byte Byte3 = 0;
byte Byte4 = 0; // Temporary storage of command and param values read from Serial port
unsigned long LongInt = 0;
int nStates = 0;
uint16_t nEvents = 0;
int LEDBrightnessAdjustInterval = 5;
byte LEDBrightnessAdjustDirection = 1;
byte LEDBrightness = 0;
byte InputStateMatrix[128][40] = {0}; // Matrix containing all of Bpod's inputs and corresponding state transitions
// Cols: 0-15 = IR beam in...out... 16-19 = BNC1 high...low 20-27 = wire1high...low 28-37=SoftEvents 38=Unused  39=Tup

byte OutputStateMatrix[128][17] = {0}; // Matrix containing all of Bpod's output actions for each Input state
// Cols: 0=Valves 1=BNC 2=Wire 3=Hardware Serial 1 (UART) 4=Hardware Serial 2 (UART) 5 = SoftCode 6=GlobalTimerTrig 7=GlobalTimerCancel
// 8 = GlobalCounterReset 9-17=PWM values (LED channel on port interface board)

byte GlobalTimerMatrix[128][5] = {0}; // Matrix contatining state transitions for global timer elapse events
byte GlobalCounterMatrix[128][5] = {0}; // Matrix contatining state transitions for global counter threshold events
boolean GlobalTimersActive[5] = {0}; // 0 if timer x is inactive, 1 if it's active.
unsigned long GlobalTimerEnd[5] = {0}; // Future Times when active global timers will elapse
unsigned long GlobalTimers[5] = {0}; // Timers independent of states
unsigned long GlobalCounterCounts[5] = {0}; // Event counters
byte GlobalCounterAttachedEvents[5] = {254}; // Event each event counter is attached to
unsigned long GlobalCounterThresholds[5] = {0}; // Event counter thresholds (trigger events if crossed)
unsigned long TimeStamps[1024] = {0}; // TimeStamps for events on this trial
byte Events[1024] = {0};
int MaxTimestamps  = 1024; // Maximum number of timestamps (to check when to start event-dropping)
int MaxTransitions = 1024;
int CurrentColumn = 0; // Used when re-mapping event codes to columns of global timer and counter matrices
unsigned long StateTimers[128] = {0}; // Timers for each state
unsigned long StartTime = 0; // System Start Time
unsigned long MatrixStartTime = 0; // Trial Start Time
unsigned long MatrixStartTimeMillis = 0; // Used for 32-bit timer wrap-over correction in client
unsigned long StateStartTime = 0; // Session Start Time
unsigned long NextLEDBrightnessAdjustTime = 0;
byte ConnectedToClient = 0;
unsigned long CurrentTime = 0; // Current time (units = timer cycles since start; used to control state transitions)
unsigned long TimeFromStart = 0;
unsigned long Num2Break = 0; // For conversion from int32 to bytes
unsigned long SessionStartTime = 0;
byte connectionState = 0; // 1 if connected to MATLAB
byte RunningStateMatrix = 0; // 1 if state matrix is running

void setup() {
	for (int x = 0; x < 8; x++) {
		pinMode(PortDigitalInputLines[x], INPUT_PULLUP);
	}
	for(int x = 1; x < 8; x++) {
		pinMode(PortPWMOutputLines[x], OUTPUT);
		analogWrite(PortPWMOutputLines[x], 0);
	}
	for (int x = 0; x < 4; x++) {
		pinMode(WireDigitalInputLines[x], INPUT_PULLUP);
		pinMode(WireDigitalOutputLines[x], OUTPUT);
	}
	for (int x = 0; x < 2; x++) {
		pinMode(BncInputLines[x], INPUT);
		pinMode(BncOutputLines[x], OUTPUT);
	}
	for (int x = 0; x < 2; x++) {
		pinMode(ValveDigitalOutputLines[x],OUTPUT);
	}
	//pinMode(ValveRegisterLatch, OUTPUT); //  SPI device latch pins
	//pinMode(SyncRegisterLatch, OUTPUT);

	pinMode(RedLEDPin, OUTPUT);
	//pinMode(GreenLEDPin, OUTPUT);
	//pinMode(BlueLEDPin, OUTPUT);

	Serial1.begin(115200);
	//SerialUSB.begin(115200);
	//SPI.begin();
	SetWireOutputLines(0);
	SetBNCOutputLines(0);
	updateStatusLED(0); // LED OFF
	ValveWrite(0);
	Timer3.attachInterrupt(handler);
	Timer3.setPeriod(100); // Runs every 100us
}
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

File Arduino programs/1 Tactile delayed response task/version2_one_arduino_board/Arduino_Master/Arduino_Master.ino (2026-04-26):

//combine Master,task and wave board. JL 11/19/2024
//from protocol 19, start optostim for 15% trials using 3 laser power levels in 3 different periods (sample, delay and response) randomly

/* Connection Circuit:
  Controller.SerialUSB <<======>> PC (data and/or debug info)
*/

#include <string.h>
#include <SD.h>        // SD card
#include <DueTimer.h>  // Timer interrupt
#include "RTClib.h"    // real time clock
#include "HX711.h"     // weighting amplifier libirary

#include "pwm_lib.h" // pwm lib for mask flashing   JL 11/19/2024
#include <Wire.h>
#include <Adafruit_MCP4725.h>

#include <SPI.h>

//*********************************************************************************************************/
//***************************************** Head-Fixation related *****************************************/
//*********************************************************************************************************/

////////////// define finite states for head-fixation //////////////
#define CHECK_TRIG          1
#define DELAY_TO_FIX        2
#define HEAD_FIXATION       3
#define HEAD_FIXATION_DELAY 4
#define CHECK_RELEASE       5
#define ESCAPE_DELAY_1000   6
#define TIMEUP_DELAY_1000   7
#define STRUGGLE_DELAY_1000 8
#define CHECK_RELEASE0      9
uint8_t timer_state = CHECK_TRIG; // init state
float weight_tmp    = 0;
unsigned long last_state_time;
unsigned long last_weight_read_time;
////////////// define finite states used in timer interrupt routines //////////////


// define protocols for the main loop
#define P_FIXATION   10 // Fixation Protocol: learn to head-fixation up to 25 sec
#define P_SAMPLE     21 // Sample Protocol:   sample period 1.2 sec
#define P_DELAY      22 // Delay Protocol:    delay period 0.3 -> 1.3 sec
#define P_OPTOSTIM   23 // Optostim Protocol: start optogenetics (during sample or delay, 20% each)

bool protocol_sent_run = 0;

// port definition
const byte portMotorLR     = 2;  // analog write channel, Left-Right
const byte portMotorFB     = 3;  // analog write channel, Forward-Backward
const byte portMotorPole   = 4;  // analog write channel, Motorized Pole
const byte portSD          = 5;  // SD card detection: low if inserted; high if removed
const byte portSwitchL     = 22;
const byte portSwitchR     = 23;
const byte portWeight_DOUT = 7;  // weight stage data
const byte portWeight_CLK  = 6;  // weight stage clock
const byte switchPin       = 49; // ToggerSwitch pin to start/pause experiment
const byte ledPin          = 13; // LED pin
const byte chipSelect      = 10; // Adafruit SD shields and modules: pin 10


using namespace arduino_due::pwm_lib;
// for go cue sound
#define PWM_PERIOD_PIN_53 27000  //3.7khz    
#define PWM_DUTY_PIN_53   13500  // 50% duty   
// for masking led             
#define PWM_PERIOD_PIN_44 10000000 // 100 ms, 10 Hz      
#define PWM_DUTY_PIN_44   100000  //  1% 
             
pwm<pwm_pin::PWMH2_PB14> pwm_pin53;
pwm<pwm_pin::PWMH5_PC19> pwm_pin44;

Adafruit_MCP4725 dac;
volatile uint16_t sample_ind = 0;
const uint16_t thorlab_flat_sine[50]  = {4079, 4031, 3951, 3842, 3704, 3540, 3353, 3145, 2919, 2680,
                                         2431, 2176, 1919, 1664, 1415, 1176, 950, 742, 555, 391, 253,
                                         144, 64, 16, 0, 16, 64, 144, 253, 391, 555, 742, 950, 1176,
                                         1415, 1664, 1919, 2176, 2431, 2680, 2919, 3145, 3353, 3540,
                                         3704, 3842, 3951, 4031, 4079, 4095
                                        };

const uint16_t thorlab_ramp_sine[200] = {4058, 3990, 3892, 3765, 3611, 3434, 3235, 3019, 2788, 2546,
                                         2297, 2045, 1794, 1547, 1309, 1082, 870, 676, 502, 352, 227,
                                         128, 57, 14, 0, 14, 56, 124, 217, 332, 469, 624, 794, 976,
                                         1167, 1364, 1564, 1763, 1957, 2144, 2321, 2484, 2632, 2761,
                                         2871, 2958, 3023, 3063, 3080, 3071, 3039, 2983, 2904, 2804,
                                         2685, 2549, 2397, 2233, 2058, 1876, 1690, 1501, 1314, 1131,
                                         955, 788, 632, 490, 363, 254, 163, 92, 41, 10, 0, 10, 40, 88,
                                         153, 235, 330, 438, 556, 682, 814, 948, 1084, 1219, 1349, 1474,
                                         1591, 1698, 1794, 1876, 1945, 1998, 2035, 2056, 2060, 2048,
                                         2019, 1975, 1916, 1844, 1759, 1664, 1559, 1447, 1328, 1206,
                                         1082, 957, 835, 715, 601, 494, 394, 304, 225, 156, 100, 56,
                                         25, 6, 0, 6, 23, 52, 90, 137, 191, 252, 318, 388, 460, 532,
                                         604, 675, 742, 804, 861, 912, 955, 991, 1019, 1037, 1047,
                                         1048, 1040, 1024, 999, 967, 929, 884, 833, 779, 721, 660,
                                         598, 536, 474, 413, 355, 299, 248, 200, 157, 119, 86, 59, 37,
                                         20, 9, 2, 0, 2, 7, 16, 27, 39, 53, 67, 81, 94, 106, 116, 125,
                                         131, 134, 134, 131, 126, 117, 106, 93, 77, 59, 40, 20, 0
                                        };

const uint16_t ultra_flat_sine[50]  = {4081, 4041, 3974, 3882, 3767, 3629, 3471, 3297, 3107, 2907,
                                       2697, 2483, 2267, 2053, 1844, 1643, 1454, 1279, 1121, 984, 868, 776,
                                       709, 669, 655, 669, 709, 776, 868, 984, 1121, 1279, 1454, 1643, 1844,
                                       2053, 2267, 2483, 2697, 2907, 3107, 3297, 3471, 3629, 3767, 3882,
                                       3974, 4041, 4081, 4095
                                      };
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

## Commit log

2020-08-21 Update Arduino_Master.ino
    without SD card, no statemachine is runing; no need to reset Arduino when changing SD card
2020-08-24 Update Arduino_Master.ino
    add SD card detection pin
2020-08-29 update Master.ino and para files
    1. human-readable prarameter files;
    2. communication module with PC;
    3. include FB final position
2020-09-03 Update Arduino_Master.ino
    minor change
2020-09-07 Update GUI
    1. Add additional panel for updating reward size on Arduino (and also add a �reward� button); V
    2. Add �read� button for the motor position and automatically update motor position when a cage is selected; �move� BF final position. V
    3. Periodically check COM port, if not available, disconnect it (or event based?). V(every second)
    4. Add �tare� weighting stage button; read threshold values; read the weight; V
2020-09-11 fix GUI/USB bug
    close COM port in GUI or unplug USB cable will not pause the system.
2020-12-21 update Arduino code
2021-01-08 update the default calibration faction in Arduino_Master.ino
2021-01-13 update iges files
    [Headbar new2.1 v2.iges, Headbar-26.5 v4.iges, Headbar.iges, Headbar.stl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]
2021-03-12 Arduino code organized by protocol
2021-08-30 Update homecage_data_plot.m
    fixed a bug in matlab analysis script "homecage_data_plot.m". The timestamp of event variable in EVENTS.mat was not properly reset when Arduino restarted more than once. Also, the timestamp unit was 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
2022-01-20 modified Arduino and Matlab code
    added the functionality to check the pole motor
2022-05-20 update the design files
    [Headbar-26.5 v4.iges, Headport.iges, Headport.stl, Headport_v6.5.iges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]
2022-06-17 update Arduino_Master.ino
    added the functionality to check the the communication between Master board and Task board and send the warning message to GUI if the communication has issue.
2022-09-22 update codes and manuals
    added the functionality to get/set the scale (calibration_factor) for the weighting stage online
2026-04-15 Reorganized files
    [Photostim related parts info.xlsx]
2026-04-20 updated version 1 programs, pats list and Matlab program. Added version 2 program.
    [PartsList.xlsx, reservoir_holder.iges, reservoir_holder.stl]

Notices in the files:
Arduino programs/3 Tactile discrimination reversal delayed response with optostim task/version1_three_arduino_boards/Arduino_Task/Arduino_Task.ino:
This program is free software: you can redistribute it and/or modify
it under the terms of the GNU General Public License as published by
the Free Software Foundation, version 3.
